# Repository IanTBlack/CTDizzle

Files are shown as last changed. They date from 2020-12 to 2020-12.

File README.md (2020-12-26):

# CTDizzle

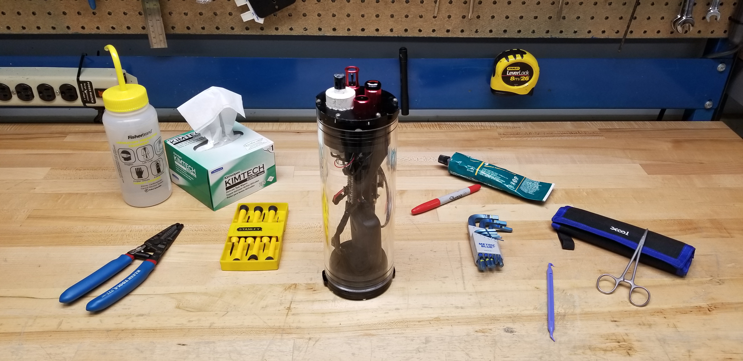
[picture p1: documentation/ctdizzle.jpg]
ctdizzle


Welcome! This is the repository for the CTDizzle, an open source CTD that is built on an Arduino platform. 
For those not familiar with the CTD instrument, it is a generic sensor type that measures water conductivity, temperature, and pressure. It is commonly used in the ocean.
By doing some math, these sensors can compute other data products like salinity, density, and depth. 
This information has a variety of applications in oceanography and fisheries research.

The CTDizzle framework is considered charityware. You can use and copy it as much as you like, but you are encouraged to make
a donation to the American Civil Liberties Union (www.aclu.org) or another charity of your choice if you find it useful.

For issues related to the CTDizzle, please use GitHub's issue tracker.

If you would like to contribute to this project, please submit a pull request or consider making your work public so that others may benefit.

For questions and more information, contact Ian Black (iantimothyblack@gmail.com). Please put "CTD" in the subject line so it doesn't go to spam.

Here are some other open source CTDs used under different applications:

Arduino-based Sonde: https://github.com/glockridge/DrifterApplication

OpenCTD: https://github.com/OceanographyforEveryone/OpenCTD

PiCTD: https://github.com/haanhouse/pictd

## CTDizzle Specifications
Maximum Sampling Rate: 1Hz

Tested Depth: 80m

Maximum Depth: 100m (Acrylic Tube), 200m (Aluminum Tube)

Conductivity Accuracy: +/- 2% (After Calibration)

Conductivity Response Time: 1s

Temperature Accuracy: +/- 0.1 degC

Temperature Response Time: 3s

Pressure Accuracy: +/- 100 mbar

Pressure Response Time: 20ms

Clock Accuracy: 29 PPM (+/- 3s per day)

Battery Life: Dependent (~60 hours @ 1Hz on a 3.7v 2200 mAh)

## How do I navigate this repository?

### ctdizzle
This folder contains the Arduino code for driving the instrument. The main sketch is the sketch titled "ctdizzle.ino". 
You may notice that there are other sketches called "temperature.ino" or "conductivity.ino". These are split files that are still part of the main sketch, but 
contain functions specific to a sensor or task. For example, "clock.ino" contains functions that will initialize the real-time clock and allow 
you to ask it for the date and time. These functions are then implemented in the setup() and loop() functions in the main sketch.

### documentation
This folder contains vendor datasheets, a spreadsheet containing a list of build materials, and a build guide.
There is also an example of a "config.txt" file, which allows you to adjust the sensor sampling rate when it is placed in the root direction of the data SD card.
Please note that many of the build materials such as solder, PLA filament, tools, and epoxy can be substituted for versions that you prefer. 
Remember that this is a guide and you can change things however you want. 
If you come up with a better solution or method, please consider contributing to the open source CTD concept by creating your own repository and instructions so that others may benefit.

### prints
This folder contains the 3D prints used in the CTDizzle. If you want to modify these parts, they are provided as .ipt files which can be used with Autodesk Inventor.
If you just want to print these parts yourself or through a vendor, you can use the .stl files and a slicer to create the necessary gcode.

Parts with the word "dremel" in the filename are intended to act as a guide when using a rotary tool to remove anodized finish on the end caps. 
These parts should be made of PLA.

Parts with the word "potting" in the filename are intended to act as a jig when using potting compound to permanently connect the conductivity probe to the endcap. 
These parts should be made out of water-soluble PVA.

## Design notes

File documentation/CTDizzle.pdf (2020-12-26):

# CTDizzle

## An Open Source CTD

### Version: 6.0.0

2020-12-26

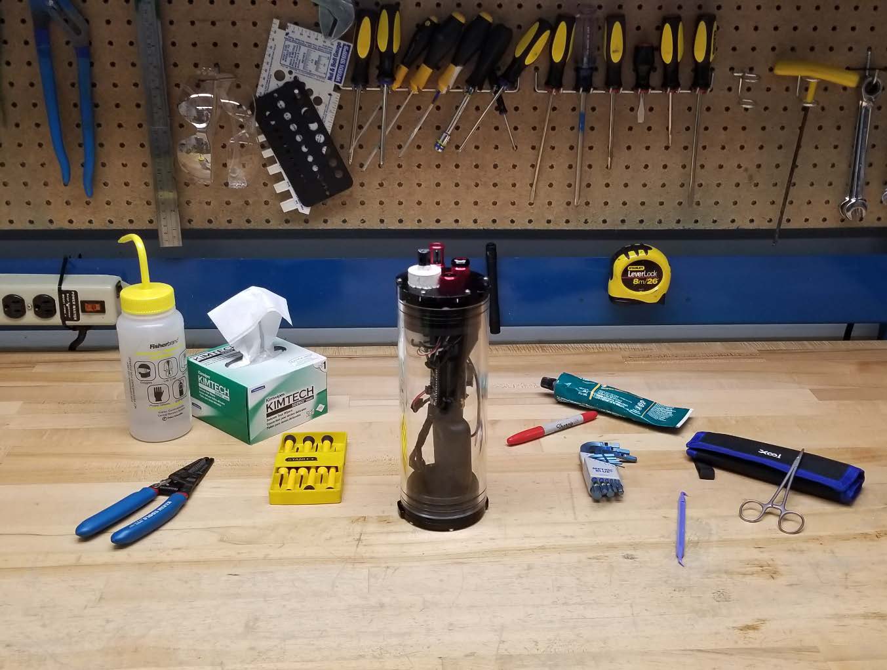
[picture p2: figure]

## Table of Contents

License | 1
Author’s Note | 1
CTDizzle Specifications | 2
Bill of Materials | 2
Other Open Source CTDs | 2
Required Skills and Experience | 2
O-rings | 2
Software Setup | 3
Arduino IDE | 3
Arduino Board | 3
Arduino Libraries | 3
Formatting the SD Card | 4
Uploading a Sketch | 4
Communication Protocols | 4
Pinouts | 5
Component Testing | 5
Building the CTDizzle | 6
Preparing the End Cap | 6
Potting the Probe | 9
Installing the Temperature, Pressure, and Switch | 12
Board Soldering | 13
3D Printed Board Mount | 14
Making the Switch Cable | 14
config.txt | 15
Bench Testing | 15
Code | 17
board.ino | 17
error_cycle_led() | 17
get_voltage() | 17
initialize_comms(bps,i2c_clock) | 17
power_board_led(state) | 17
power_leds(state) | 17

wait_for_serial(seconds) | 17
clock.ino | 17
get_datetime() | 17
get_unixtime() | 18
initialize_rtc() | 18
conductivity.ino | 18
get_conductivity() | 18
power_ec_led(state) | 18
ctdizzle.ino | 18
setup() | 18
loop() | 18
eos80.ino | 18
compute_depth(relative_pressure,latitude) | 18
compute_salinity(conductivity,temperature,relative_pressure) | 19
compute_density_anomaly(salinity, temperature, relative_pressure) | 19
pressure.ino | 19
get_absolute_pressure() | 19
get_relative_pressure(atmospheric) | 19
initialize_pressure() | 19
sd.ino | 19
initialize_logger() | 19
log_data(dt,ec,t,p,v) | 19
make_directory() | 19
make_file() | 20
read_config() | 20
set_file_creation_datetime() | 20
temperature.ino | 20
get_temperature() | 20
initialize_temperature() | 20
Conductivity Calibration | 20
Temperature Compensation | 20
Things to Think About | 21
Corrosion | 21

Batteries and Charging | 21
Data Quality | 21

1

## License

MIT License

Copyright (c) 2017 Ian Black

Permission is hereby granted, free of charge, to any person obtaining a copy of this software and associated documentation files (the "Software"), to deal in the Software without restriction, including without limitation the rights to use, copy, modify, merge, publish, distribute, sublicense, and/or sell copies of the Software, and to permit persons to whom the Software is furnished to do so, subject to the following conditions:

The above copyright notice and this permission notice shall be included in all
copies or substantial portions of the Software.

THE SOFTWARE IS PROVIDED "AS IS", WITHOUT WARRANTY OF ANY KIND, EXPRESS OR IMPLIED, INCLUDING BUT NOT LIMITED TO THE WARRANTIES OF MERCHANTABILITY, FITNESS FOR A PARTICULAR PURPOSE AND NONINFRINGEMENT. IN NO EVENT SHALL THE AUTHORS OR COPYRIGHT HOLDERS BE LIABLE FOR ANY CLAIM, DAMAGES OR OTHER LIABILITY, WHETHER IN AN ACTION OF CONTRACT, TORT OR OTHERWISE, ARISING FROM, OUT OF OR IN CONNECTION WITH THE SOFTWARE OR THE USE OR OTHER DEALINGS IN THE SOFTWARE.

## Author’s Note

You can use and copy any part of the CTDizzle as much as you like, but you are encouraged to make a donation to the American Civil Liberties Union (www.aclu.org) or any charity of your choice if you find it useful.
This guide operates under the assumption that you are using parts found within the Bill of Materials. This guide is not foolproof and the author acknowledges that there are likely better ways to build an open source CTD. The author has also made many expensive mistakes while iterating each build and recognizes that builders may make similar mistakes if not treading lightly. If you are unsure of how to perform a task, please take the time to research methods and practice skills. If you come up with a simpler or better way to complete a task, please share that knowledge!
If at any time you have questions, concerns, or need guidance, please to do not hesitate to contact: Ian Black
iantimothyblack@gmail.com

## CTDizzle Specifications

Maximum Sampling Rate: 1Hz
Tested Depth: 80m
Maximum Depth: 100m (Acrylic Tube), 200m (Aluminum Tube) Conductivity Accuracy: +/- 2% (After Calibration)
Conductivity Response Time: 1s
Temperature Accuracy: +/- 0.1 degC
Temperature Response Time: 3s
Pressure Accuracy: +/- 100 mbar
Pressure Response Time: 20ms
Clock Accuracy: 29 PPM (+/- 3s per day)
Battery Life: Dependent (~60 hours @ 1Hz on a 3.7v 2200 mAh)

## Bill of Materials

A complete list of parts used, cost, and quantities can be found in the CTDizzle GitHub repository under the documentation folder in a file called BoM.ods.

## Other Open Source CTDs

Arduino-based Sonde: https://github.com/glockridge/MooredApplication
Oceanography For Everyone OpenCTD: https://github.com/OceanographyforEveryone/OpenCTD PiCTD: https://github.com/HaanHouse/PiCTD

## Required Skills and Experience

The construction of any open source CTD requires some experience using tools such as a soldering iron, wire strippers, drill, screwdriver, and wrench. If you are unfamiliar with soldering, it is highly
recommended that you practice the lineman’s splice on a piece of scrap wire and through-hole soldering on a piece of protoboard.
The CTDizzle in particular requires some experience 3D printing with Polylactic Acid (PLA) and Polyvinyl Alcohol (PVA) filaments. If you are following along with this guide, you will also be required to mix and place epoxies.
O-rings
The Blue Robotics components of this CTD build require you to be familiar with O-ring inspection and installation. Clean and greased O-rings are paramount to the success of a CTD deployment in the ocean. To inspect and install an O-ring…
1. Wash and dry your hands.
2. Use isopropyl alcohol and lint-free wipes to clean the O-ring.
3. Under a light source, lightly stretch the O-ring and use your fingers to feel and observe for any damage.
4. Apply a light amount of silicone grease to the O-ring before installation.
5. Use an O-ring pick to install the O-ring.

## Software Setup

Arduino IDE
The Arduino Integrated Development Environment (IDE) is simple to use and allows you to quickly upload code to a board that understands Arduino. If you are new to Arduino, it is recommended that you set up the Arduino IDE using the default directories that the download wizard creates.
To install the IDE…
1. Go to https://www.arduino.cc/en/software to download the Arduino IDE installer that works best with your operating system.
2. Follow the installation wizard.
3. Hooray! You can now use the IDE.

Arduino Board
There are many different types of Arduino boards out there and not all are supported by default within the Arduino IDE. In order to get the Adafruit Feather M0 Basic Proto to work, we need to make sure the IDE knows what to look for by installing the right package.
To set up the M0…
1. Open the Arduino IDE.
2. Navigate to Tools > Board > Boards Manager.
3. In the search bar, type in Adafruit SAMD Boards
4. In the window, select Adafruit SAMD Boards. Confirm the Adafruit Feather M0 is in the list of boards included in the package.
5. Ensure the version is the most recent version.
6. Select Install.

Arduino Libraries
The CTDizzle requires the installation of Arduino libraries that help you communicate with each sensor. Libraries contain sets of functions that simplify the development process and allow you to focus more on higher level coding. In order to operate the CTDizzle, you will need to install several third-party libraries. Conveniently, they can be installed via the Arduino IDE.
Table 1: Third-party Arduino Libraries
Library Name | Developer | GitHub Repo
RTClib | Adafruit | https://github.com/adafruit/RTClib
BlueRobotics MS5837 Library | Blue Robotics | https://github.com/bluerobotics/BlueRobotics_MS5837_Library
BlueRobotics TSYS01 Library | Blue Robotics | https://github.com/bluerobotics/BlueRobotics_TSYS01_Library
To install these libraries…
1. Open the Arduino IDE.
2. Navigate to Tools > Manage Libraries.
3. Search for each library by name.
4. Install the most recent version.

Formatting the SD Card
It is also necessary to format the microSD card so that it can be used to store data. You can do this using the native formatter utility for your operating system, but it is recommended that you utilize the SD Memory Card Formatter tool developed by the SD Association.
To download the SD Memory Card Formatter…
1. Go to https://www.sdcard.org/downloads/formatter/
2. Download the correct tool for your operating system.
3. Follow installation instructions.
To format your card…
1. Insert your card into your computer. Make sure it appears in your file explorer.
2. Open the SD Card Formatter tool.
3. Select your card.
4. Select Quick Format.
5. Name your card if you want.
6. Select Format.

Uploading a Sketch
Uploading a code (aka sketch) is simple to do with the Arduino IDE. To upload a sketch…
1. Open the Arduino IDE.
2. Make sure the sketch you want to upload is in the window.
3. Navigate to Tools > Board and select Adafruit Feather M0.
4. Navigate to Tools > Port and select the port that has the Adafruit Feather M0.
5. Navigate to Sketch > Upload. (or hit CTRL + U, or select the right-pointing arrow)
6. Wait for the sketch to compile and upload!

## Communication Protocols

All the sensors in this CTD build use the inter-integrated circuit (I2C) serial communication protocol. This means that each sensor can be on the same send and receive data lines. Each sensor has its own address, which prevents confusion when talking to multiple sensors. For the sake of simplicity, the operating code for this CTD waits for one sensor to respond and send data before talking to the next sensor.
The SD card module of the Adalogger Featherwing operates under the Serial Peripheral Interface (SPI) protocol. Like I2C, multiple sensors can be connected on the same lines send and receive lines. However, SPI requires that each sensor be connected to its own chip select, thus taking up more pins compared to I2C. Conveniently, the SD card module in this build is the only component that operates under SPI.
The Atlas Scientific EC EZO can operate under I2C or Universal Asynchronous Receive Transmit (UART). By default, the EC EZO is shipped in UART mode. You can review the Atlas Scientific manual to change it to I2C mode either via software or manually. Each protocol has its advantages and disadvantages, but the CTD operating code assumes that the EC EZO is in I2C mode.

## Pinouts

Each sensor wire/pin should be connected to the controller board pin as described by the table below. Note that each Blue Robotics sensor is 3.3V tolerant. If you connect one of those sensors to a 5V pin, you risk damaging it. The Atlas Scientific EC EZO can be connected to 3.3V or 5V. The Adalogger Featherwing SD module is automatically connected when you stack it on top of the Feather M0. The chip select just needs to be specified in the operating code.
Table 2: Sensor Pinouts
Blue Robotics TSYS01 Temperature Sensor | Adafruit Feather M0
Black Wire | GND
Red Wire | 3V
Yellow Wire | SDA
Green Wire | SCL
Blue Robotics MS5837 Pressure Sensor | Adafruit Feather M0
Black Wire | GND
Red Wire | 3V
Yellow Wire | SDA
Green Wire | SCL
Atlas Scientific EC EZO or Carrier Board | Adafruit Feather M0
GND | GND
VCC | 3V
SDA/TX | SDA
SCL/RX | SCL
Adalogger Featherwing SD Module | Adafruit Feather M0
CS | 10

## Component Testing

# Please inspect and test each component

before soldering and install.

# Vendor guides can be found in the documentation folder of the GitHub

repository.

## Building the CTDizzle

Preparing the End Cap
In order to pot the Atlas Scientific Conductivity probe to the end cap, you must drill out one of the holes to 12mm. In the following pictures, the side facing up is the “external” side and the side facing down is the “internal” side. “External” implies that it is going to be exposed to seawater.
In the left image orientation, the 12mm hole was drilled into the upper right hole using a 12mm drill bit. The hole was then deburred. You will want to test fit the conductivity probe in the newly drilled hole. If you are unable to insert it, use a round file to increase the diameter of the hole slightly. The conductivity probe should fit snugly and require some force to insert and remove.

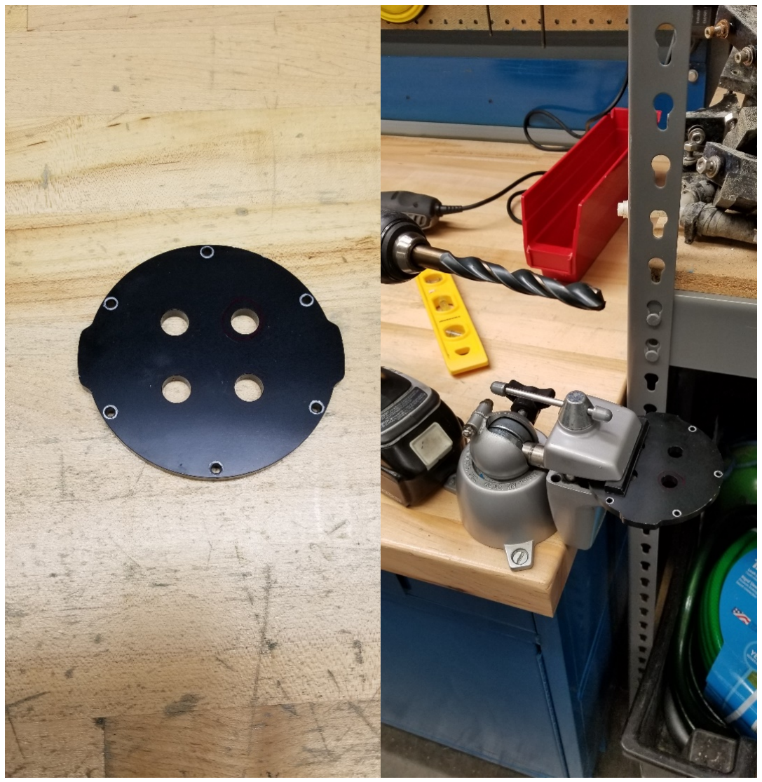
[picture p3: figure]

Figure 1: End cap 12mm hole placement.

Next attach the dremel_internal and dremel_external 3D prints to the endcap using some M3 screws and nuts. Notice that the internal and external 3d prints result in holes that are different shapes. The internal print will produce an irregularly shaped outline to accommodate the internal diameter of the end cap flange.

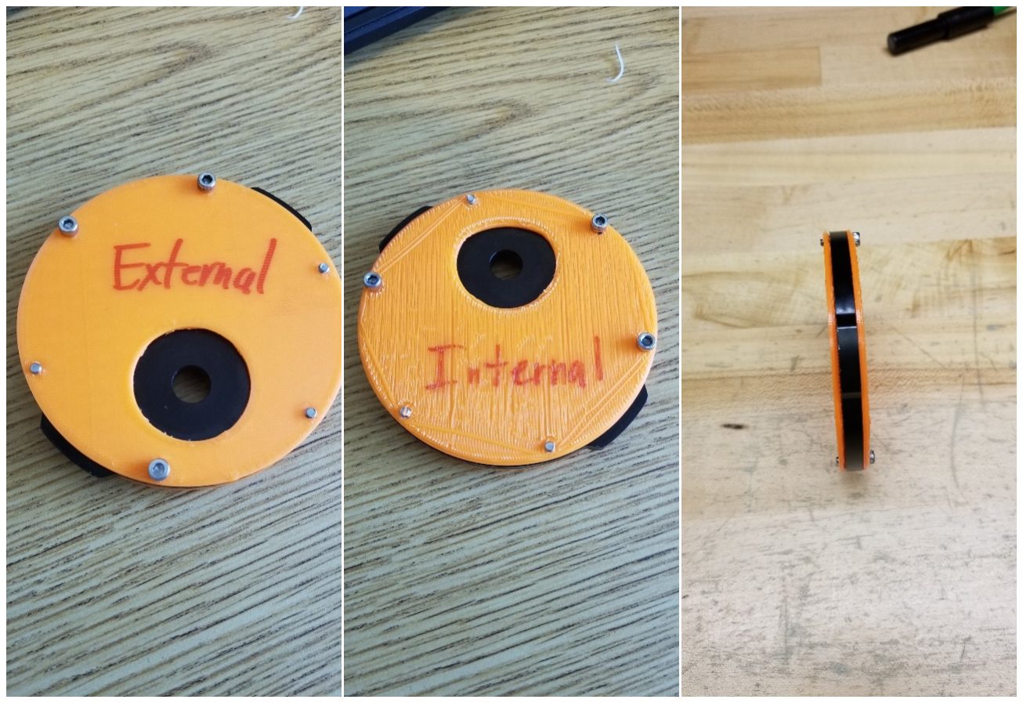
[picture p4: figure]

Figure 2: Rotary tool jig placement.

Using a Dremel or similar rotary tool, remove the exposed anodization. This can be done using a grindstone bit or sandpaper attachment. You should remove the anodization to the point where you see exposed aluminum and the surface finish is rough. This will facilitate better adhesion of the epoxy used to hold the conductivity probe in place.

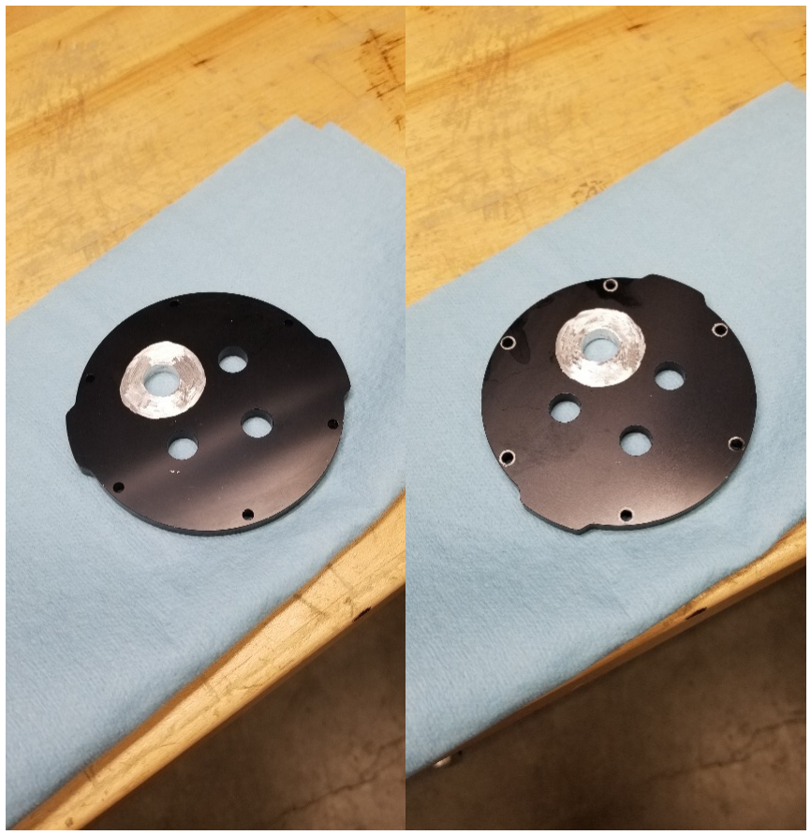
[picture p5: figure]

Figure 3: End cap after removal of anodization.

Potting the Probe
Test fit the probe in the 12mm hole. Using the PVA (potting_*) prints as guides, mark on the probe the height of the prints. Remove the probe from the end cap.
Using sandpaper, rough up the portions of the probe that will be in contact with epoxy. This will ensure better adhesion.
Clean the end cap and probe with isopropyl alcohol. Apply masking or electrical tape around the edge of the raw aluminum on both sides. This will help keep the potting compound in the appropriate area in case the PVA potting jig warps during use. Install the probe and wrap the sensor area in electrical tape to prevent epoxy leakage.

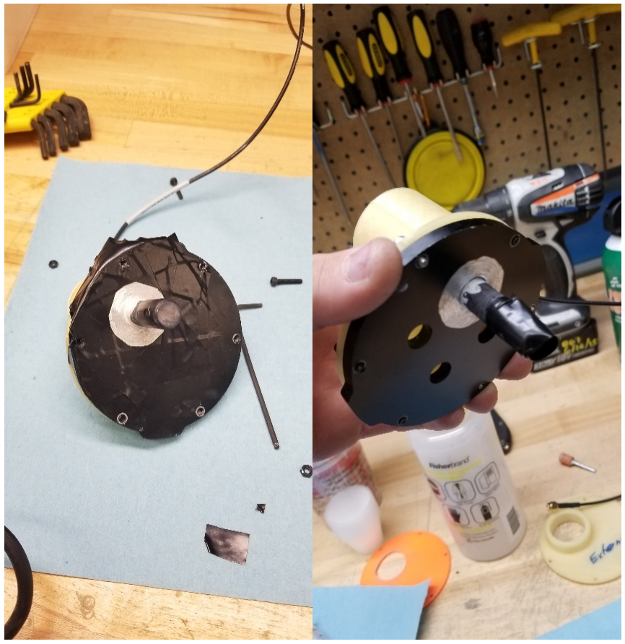
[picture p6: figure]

Figure 4: Taping of area around bare aluminum and probe end.

After installing the probe, install the potting_internal 3D print using some M3 screws to secure it to the end cap. Make sure it lines up with the correct side. You can support the end cap using a cup or mug. Once it is installed, mix and apply enough epoxy to fill the void to the rim. If bubbles appear, use a toothpick to remove them. Allow the epoxy to cure for 24-48 hours. Check the epoxy after a couple of hours to make sure that it has not leaked below the PVA jig. If it has, remove the jig and use isopropyl alcohol to clean up the epoxy.
After the internal side has cured, repeat the process with the external side.

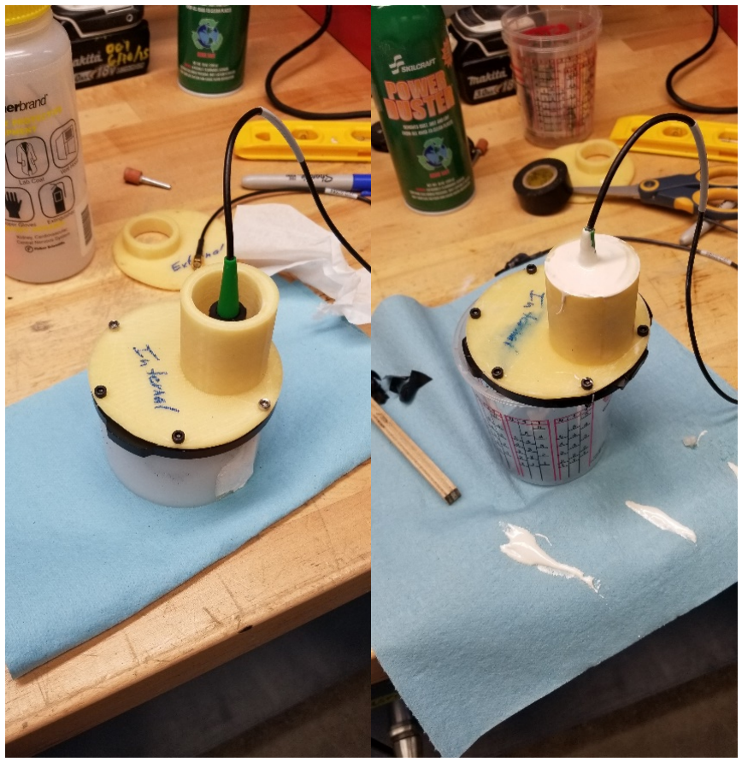
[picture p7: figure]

Figure 5: Installation of PVA jigs for epoxy application.

Once both sides have cured, place the setup up in a container of water. You may have to replace the water every few hours or so. Once the PVA 3D prints have dissolved way, clean up the epoxy with a scotch brite pad and a file to remove any burrs. Test fit the end cap flange to ensure they fit well together. If the epoxy make its way underneath the jig while curing, you can use a pair of hemostats or metal pick to remove the excess. Take care to not scratch the surface the end cap O-ring will seal to.

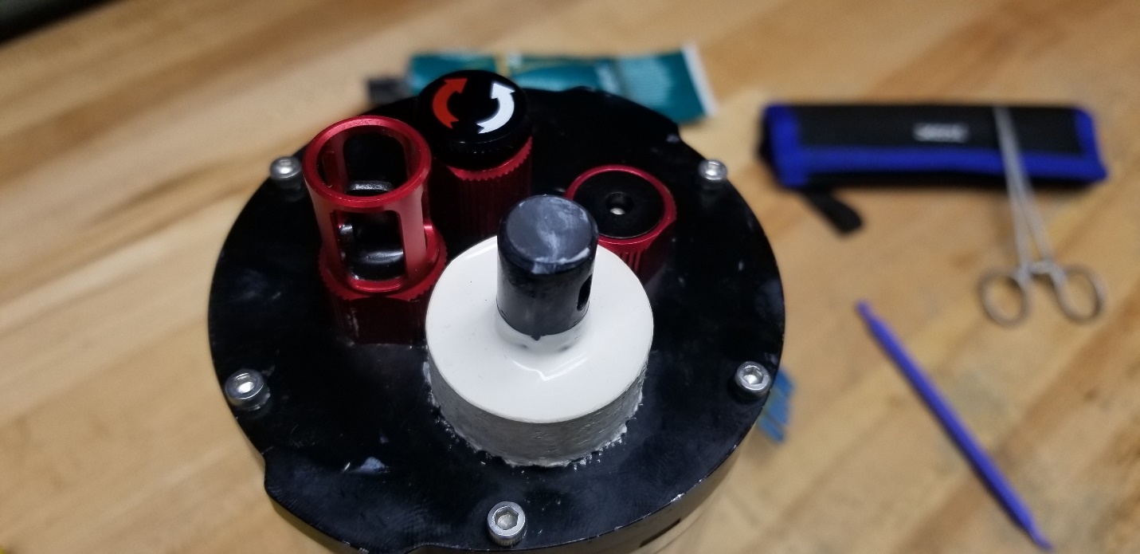
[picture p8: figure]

Figure 6: View of the external epoxy.

Installing the Temperature, Pressure, and Switch
Clean the end cap using isopropyl alcohol. Ensure the O-rings are clean and greased. The O-rings should be within the groove of each bulkhead and on the side of the end cap that is exposed to seawater. Insert each component into the end cap and add the nut. Tighten using a Blue Robotics tool or a crescent wrench. They should be tightened enough that you observe no gap between the bulkhead and end cap. In these pictures, the DF13 connectors are removed from the sensors. If you do not want to remove them, Blue Robotics offers a DF13->pinout board. If you opt to remove the connectors, cut them off as close to the connector as possible.

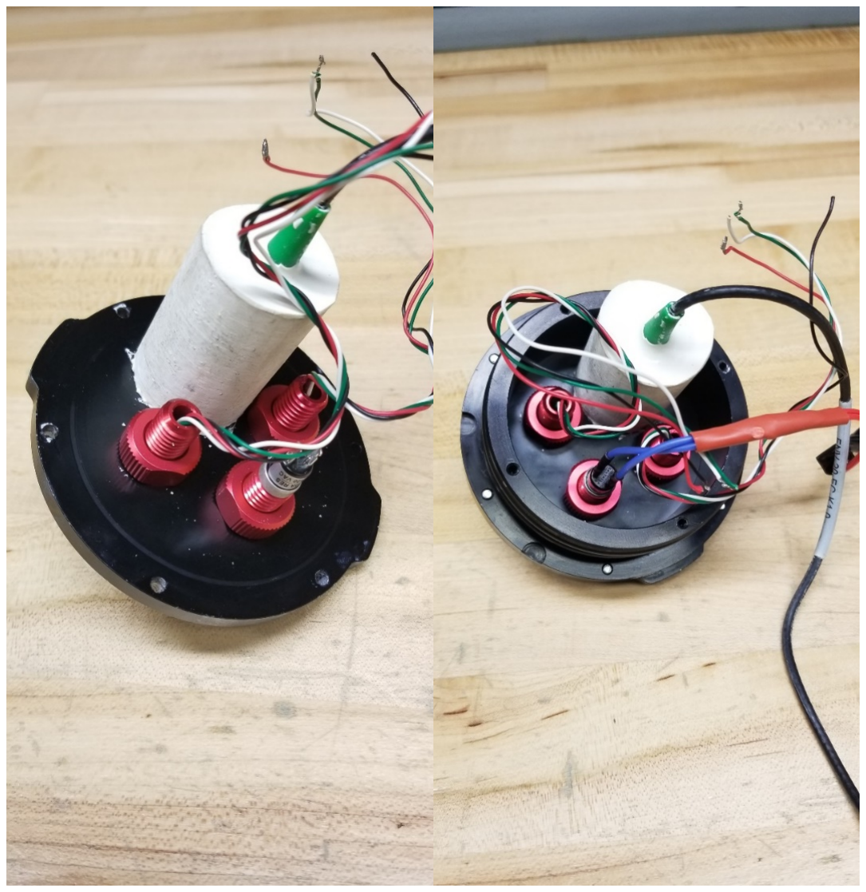
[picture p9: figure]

Figure 7: Installation of Blue Robotics sensors and switch.

Board Soldering
For access to the prototyping area, the M0 can be stacked on top of the Adalogger using stacking headers. The use of short feather headers allows for a more compact footprint. The first step is to solder a set of short male feather headers to the M0. A terminal block set can be installed in the prototyping area to make it easier to connect sensor wires to the board. You will need to solder wires from the GND, 3V, SCL, and SDA pins to the terminal block so that the conductivity, temperature, and pressure sensors can be connected to the board. The following pictures show one way to do that.

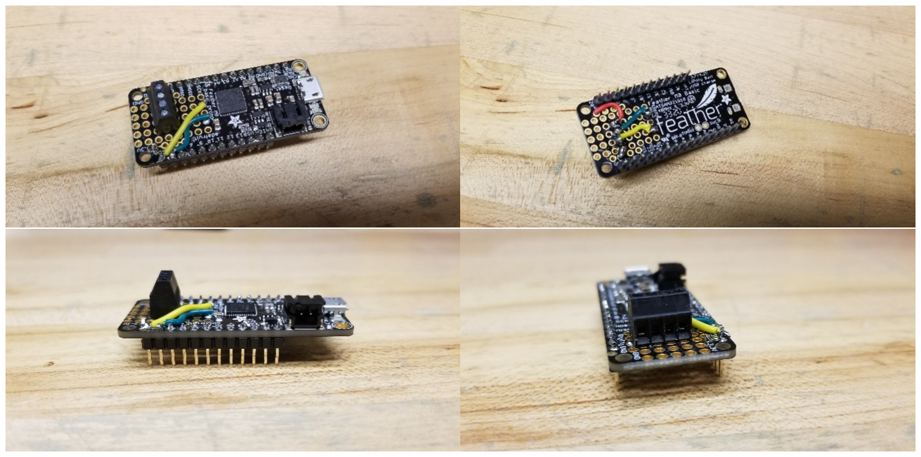
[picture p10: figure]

Figure 8: Soldering of male headers, wires, and terminal block to the Adafruit Feather M0 Proto

The Adalogger will stack below the M0. Next, solder a set of short female feather headers to the Adalogger. The following pictures show what the orientation should look like.

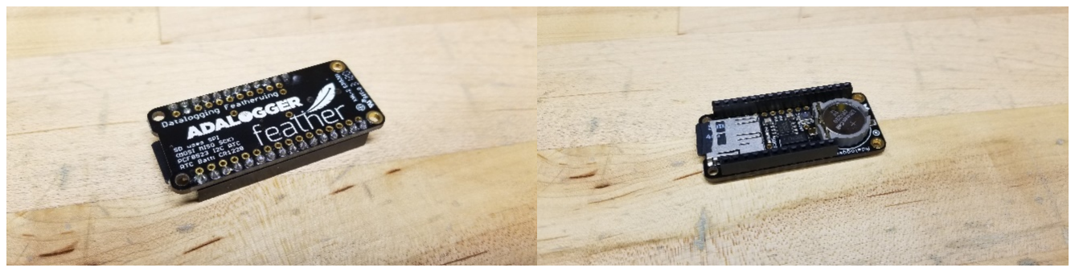
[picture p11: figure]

Figure 9: Soldering of female headers to the Adalogger Featherwing.

3D Printed Board Mount
The 3D printable mount allows you to mount the controller board stack and the Atlas Scientific EZO Isolation Board to the sensor flange. The mount is attached to the flange using 11mm M3 screws. The boards are attached to the mount using M2.5 thread nylon standoffs. This is one method of many to mount the electronics inside of the pressure case. Feel free to modify the drawings to suit your needs.

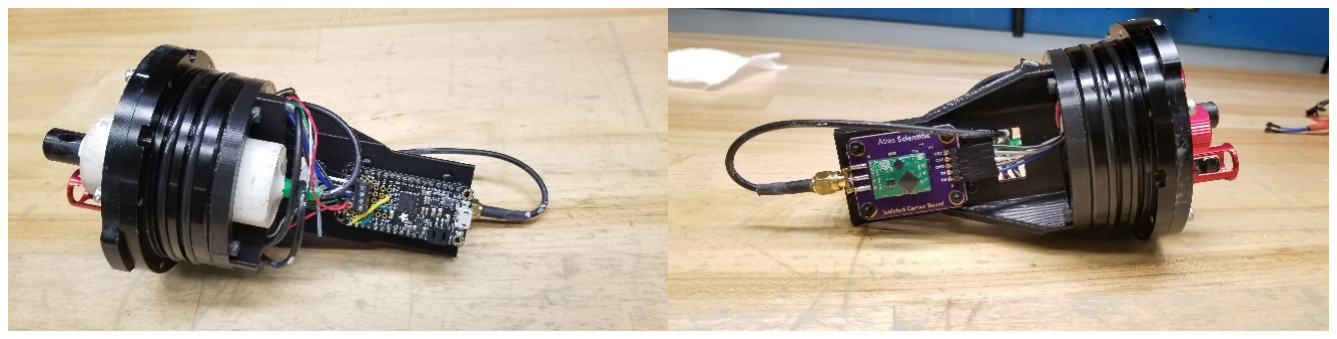
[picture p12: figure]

Figure 10: Attachment of the 3D printed mount. Making the Switch Cable
The addition of the Blue Robotics switch allows you to power cycle the sensor. This can help with conserving battery life and provides the ability to differentiate between profiles if using the CTD in a profiling fashion. If you are using a 5V rechargeable battery pack, you will need to splice the Blue Robotics switch wires into the V+ line on the USB cable.

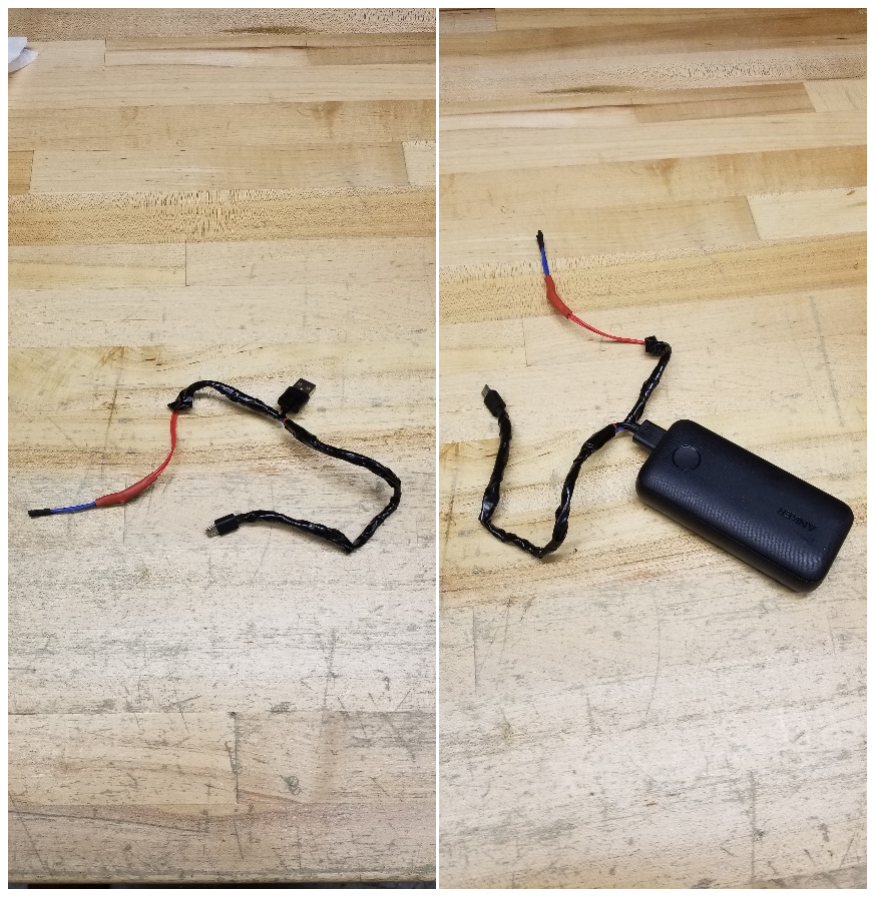
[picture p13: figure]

Figure 11: Example of a 5V USB cable splice to the switch

## config.txt

You have the option of placing a config.txt file on your microSD card. This file should contain only an integer on the first line that represents the number of seconds to wait in between samples. If unable to interpret the file, or if it doesn’t exist, the CTD will default to one sample per second.
If you want to adjust the sampling rate to one sample every 3 hours, you will need to create a config.txt file like the screenshot below and then place it in the root directory of your SD card.

## Bench Testing

Once all the wiring is complete. Upload the ctdizzle sketch to your board.
Navigate to Tools > Serial Monitor. The setup sequence will begin once serial communication is established or after 30 seconds (whichever comes first). You will see something like the screenshot below. Confirm that the clock time and sensor values are appropriate.

The first column is the datetime.
The second column is the conductivity, which should be zero if the sensor is in air.
The third column is the temperature. If this value is negative, check your SCL/SDA orientation.
The fourth column is the pressure, which should be zero or near zero in air.
The fifth column is the battery voltage. Since we are connected to the USB, this value is the voltage on the vbatt pin.

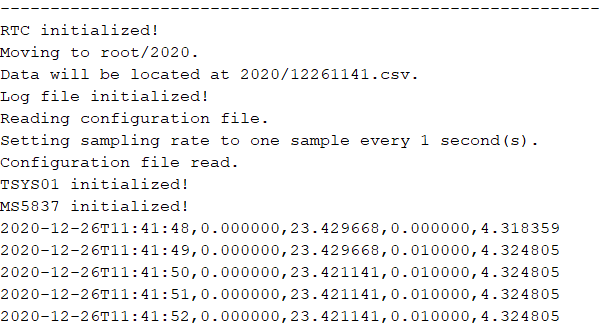
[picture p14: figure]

After you have let the unit run for a minute or so, disconnect the power and then insert the SD card into a reader device attached to a computer. Once you open the drive folder, the contents should look similar to the screenshot below. If you didn’t create a config.txt file previously, it won’t exist. If the year isn’t 2020, then the folder name will also be different.

Opening the folder titled by year will show files for each time you turned the unit on.

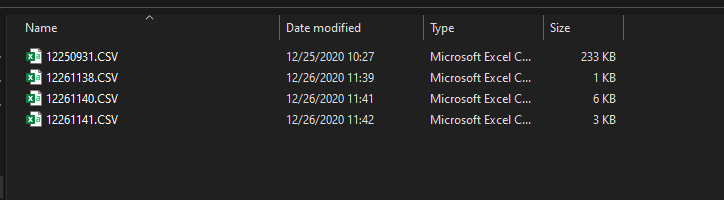
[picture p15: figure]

If we open the 12261141.CSV file, we see data that matches the output from the serial monitor.

## Code

The main sketch for operation is the ctdizzle.ino file found in the ctdizzle folder. You’ll notice that there are several .ino files in this folder, but they are all actually part of the same sketch! For more details on each function, please read the comments in the code.

board.ino
Upon upload, this sketch brings in the Wire and SPI libraries that allow the M0 to communicate to the sensors and clock.
error_cycle_led()
This function will turn the board LED on pin 13 on for 1 second and then off for 1 second.
It is usually put inside of a never-ending while loop and used as a visual indicator for an error. get_voltage()
This function will calculate the battery voltage on the vbatt_pin. For the Feather M0, this is pin A7. The voltage is returned as a float.
initialize_comms(bps,i2c_clock)
This function initialize serial communications so that the board can talk to sensors.
bps refers to bits per second, or the baud rate for serial communication between the board and the host computer. i2c_clock refers to the clock frequency for I2C communication. power_board_led(state)
This function will turn the board LED on pin 13 on or off, given a state. The state is either “ON” or “OFF”.
power_leds(state)
This function will turn the board and EC EZO LEDs on or off, given a state. The state is either “ON” or “OFF”.
wait_for_serial(seconds)
This function will wait for a serial connection to a terminal program on the host computer for X number of seconds before proceeding. While it is waiting, the board LED will cycle.

clock.ino
Upon upload, this sketch brings in the RTClib library that allows for communication with the clock on the Adalogger.
get_datetime()
This function returns the current date and time as a string in ISO-8601 format (YYYY-mm-ddTHH:MM:SS).

get_unixtime()
This function returns the current date and time as an integer in the number of seconds since 1970-01-01 00:00:00
initialize_rtc()
This function initializes the real time clock on the Adalogger. If the RTC has lost power and the board detects a serial connection to the computer, time is automatically updated. If no communication occurs with the clock, then the board error cycles the LED.

conductivity.ino
get_conductivity()
This function requests conductivity from the EC EZO and returns it as a float. There is a built-in wait time of 600ms to allow the EC EZO to perform its conversion.
power_ec_led(state)
This function will turn the EC EZO LED on or off, given a state. The state is either “ON” or “OFF”.

ctdizzle.ino
This is the main sketch for CTD operation. It contains the setup and loop functions. atmospheric_pressure is globally declared because it is used to “zero” the pressure sensor. This is of course operating under the assumption that you turned the sensor on above water and near sea level. interval is also globally declared. This value is pulled from a config.txt file located on the SD card. If no config file is found, then the interval defaults to 1. The CTD will then sample once per second.
setup()
This function initializes all sensors and sets up logging files.
loop()
This function will request data from each sensor and then save it to a log.
At the beginning of the loop, the number of milliseconds since the microcontroller started is recorded, then operations are performed, and the number of milliseconds since the microcontroller started is sampled again. The difference between these values is then subtracted from the interval value. This provides more accurate timing between samples.

eos80.ino
This sketch provides functions for computing depth, salinity, and density anomaly. compute_depth(relative_pressure,latitude)
Computing depth requires that relative pressure be in decibars and that the latitude be defined. The return for this function is depth in meters.

compute_salinity(conductivity,temperature,relative_pressure)
Computing salinity requires conductivity in uS/cm, temperature in degC, and relative pressure in decibars. The return for this function is salinity in PSU.
compute_density_anomaly(salinity, temperature, relative_pressure)
Computing density requires salinity, temperature, and relative pressure. The return for this function is the density anomaly relative to 1000 kg/m3.

pressure.ino
This sketch provides functions for controlling the MS5837 pressure sensor.
get_absolute_pressure()
This function will return the total pressure reading (including the pressure exerted by the atmosphere). The return is in milibars. There is a built in delay of 50ms to allow for the pressure sensor to perform conversions.
get_relative_pressure(atmospheric)
This function removes consideration of atmospheric pressure and returns the water column pressure in decibars. You will need to supply the atmospheric pressure. This can be done by taking a pressure sample on start-up, assuming the unit is above water, or by using a standard atmospheric pressure of 1013.25 mbar.
initialize_pressure()
This function initializes the pressure sensor.

sd.ino
This sketch provides functions for setting up the SD card and creating log files. Upon upload, the necessary libraries and files are defined.
initialize_logger()
This function initializes the SD card module, reads the config file (if it exists), makes a new directory(if needed) and creates a new file to log to.
log_data(dt,ec,t,p,v)
This function logs data to a csv file. To alter the order of logging you will need to modify the function defined in loop(), the formatting in log_data() and the header string in make_file(). make_directory()
This function creates a new directory on the SD card that is titled by the current year. If the folder already exists, then nothing exciting happens.

make_file()
This function creates a new log file on power cycle. Data is saved to this file in a format defined by the header string in this function and the log_data() function. The file is named by the date and time that it was created. It is in the format of mmddHHMM.csv
read_config()
This function reads from a simple configuration file (config.txt) located in the root directory of the SD card. Currently, this config.txt file can only consist of a single integer, which then determines the number of seconds in between samples. If no config.txt file is found, the number of seconds in between samples defaults to 1s.
set_file_creation_datetime()
This is a function that assigns a date and time attribute to the created log file so that it is easier to identify datafiles when using a file explorer. This function is called within the initialize_logger() function.

temperature.ino
This sketch contains functions for driving the TSYS01 temperature sensor.
get_temperature()
This function requests temperature from the TSYS01. There is a built-in 50ms delay to allow the sensor to perform its conversion.
initialize_temperature()
This function initializes the TSYS01.

## Conductivity Calibration

You can calibrate the conductivity sensor using methods as outlined by the Atlas Scientific User Manual. Atlas Scientific provides code examples on GitHub. https://github.com/Atlas-Scientific/Ezo_I2c_lib

Temperature Compensation
It should be noted that temperature plays a significant role in calibrating a conductivity probe. The CTDizzle code does not implement temperature compensation for conductivity, so that functionality must be added. The Atlas Scientific EC EZO offers temperature compensation of conductivity, but anecdotally this has been problematic. Atlas Scientific has not provided information on how this compensation is performed.

## Things to Think About

Corrosion
The Blue Robotics end caps are made of anodized aluminum and the provided screws are made of 316 stainless steel. Two contacting dissimilar metals in seawater effectively form a battery. The metal lower on the galvanic series scale (the anode) will corrode before the metal higher in the series (the cathode). Stainless steel is higher on the scale than aluminum so the aluminum end cap will corrode first. Anodization of the aluminum helps prevent this a little, but over time repeated removal and installation of the stainless screws can damage the anodization, exposing raw aluminum to seawater. It is recommended that you inspect the end cap before each deployment for signs of corrosion. You can also prevent corrosion by adding an anode that is lower on the galvanic series than aluminum. A chunk of zinc is a common anode used on oceanographic equipment.
Anoxic corrosion of the 316 stainless screws is also possible. Anoxic refers to a lack of oxygen in the seawater. Stainless will severely corrode in anoxic environments if left for a significant amount of time. If the CTD has been deployed for a long amount of time, it is recommended that you inspect the screws for corrosion. A corroded screw can lead to loosening of the end cap and reduction in the effectiveness of the O-ring, leading to flooding of the sensor.

Batteries and Charging
The Adafruit Feather M0 has a built-in 3.7V Lithium Polymer battery charger. In order to charge a battery, the board must be connected to a 5V source via the microUSB connector. The board can also be powered with an 5V source, such as a rechargeable battery pack intended for charging cell phones. These types of battery packs must be connected to the microUSB connector. These above directions describe how to create a switch cable for a 5V rechargeable battery pack, but you can do the same for a 3.7V LiPo. The JST Battery Extension Cable found in the Bill of Materials will allow you to do this without modifying the battery cable.
This iteration of the CTDizzle does not consider power savings. You can likely improve battery life by forcing the controller and peripherals to enter low power states when not in use.

Data Quality
If you are familiar with commercially available CTDs, you’ll notice that the CTDizzle does not compare in terms of accuracy, response times, and resolution. This problem does not necessarily preclude any open source CTD from being used in scientific study, but it does pose a challenge, particularly where high accuracy and resolution is needed. Currently there is a lack of robust calibration and quality
conformance procedures for the CTDizzle and other open source CTDs.

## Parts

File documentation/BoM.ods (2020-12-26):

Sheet: Parts
Prices as of 2020-12-26
Total | $797.60
Part/Consumable | Price Per Unit (USD) | Quantity | Subtotal (USD) | Note
Adafruit M0 Basic Proto | $19.95 | 1 | $19.95 | SAMD21
Adafruit Adalogger Featherwing | $13.95 | 1 | $13.95 | SD and RTC
Atlas Scientific Conductivity Kit K1.0 (https://atlas-scientific.com/kits/conductivity-k-1-0-kit/) | $214.99 | 1 | $214.99 | Includes mini probe, jumpers, driving circuit, isolation board, and calibration standards.
Blue Robotics Celsius Temperature Sensor (https://bluerobotics.com/store/sensors-sonars-cameras/sensors/celsius-sensor-r1/) | $60.00 | 1 | $60.00 | Includes O-ring.
Blue Robotics Bar30 Pressure Sensor (https://bluerobotics.com/store/sensors-sonars-cameras/sensors/bar30-sensor-r1/) | $72.00 | 1 | $72.00 | Includes O-ring.
Blue Robotics 3” Flange (https://bluerobotics.com/store/watertight-enclosures/3-series/o-ring-flange-3-series/) | $24.00 | 2 | $48.00 | Includes O-rings.
Blue Robotics 3” End Cap – No Holes (https://bluerobotics.com/store/watertight-enclosures/3-series/wte3-m-end-cap-r1/) | $10.00 | 1 | $10.00 | Includes O-rings.
Blue Robotics 3” End Cap – 4 Holes (https://bluerobotics.com/store/watertight-enclosures/3-series/wte3-m-end-cap-4-hole-r1/) | $12.00 | 1 | $12.00 | Includes O-rings.
Blue Robotics 3” Acrylic Tube – 11.75” (https://bluerobotics.com/store/watertight-enclosures/3-series/wte3-p-tube-12-r1/) | $86.00 | 1 | $86.00
Blue Robotics Switch (https://bluerobotics.com/store/comm-control-power/switch/switch-10-5a-r1/) | $15.00 | 1 | $15.00 | Includes O-rings and connector wires.
Loctite Marine Epoxy (https://www.amazon.com/gp/product/B00KH62K50/ref=ppx_yo_dt_b_asin_title_o07_s00?ie=UTF8&psc=1) | $5.50 | 6 | $33.00 | 0.85 Fl Oz Syringe
Hex M3 Nuts/Bolts Pack (https://www.amazon.com/gp/product/B078V3YCF6/ref=ppx_yo_dt_b_asin_title_o09_s00?ie=UTF8&psc=1) | $16.00 | 1 | $16.00 | Multiple uses. For securing 3D print to flange. Can ask Blue Robotics for extras if you don’t want to buy the whole pack.
SainSmart 1.75mm PVA – 0.5kg (https://www.amazon.com/gp/product/B00SSXAET8/ref=ppx_yo_dt_b_asin_title_o06_s00?ie=UTF8&psc=1) | $41.06 | 1 | $41.06 | Multiple prints. Water soluble.
Left-angle MicroUSB (https://www.amazon.com/gp/product/B003YKX6W2/ref=ppx_yo_dt_b_asin_title_o07_s00?ie=UTF8&psc=1) | $3.45 | 1 | $3.45 | Use this to hook up a 5v power pack if you go that route.
Hatchbox 1.75mm PLA – Any Color (https://www.amazon.com/HATCHBOX-3D-Filament-Dimensional-Accuracy/dp/B00J0EE1D4) | $20.00 | 1 | $20.00 | Multiple prints.
Kester 44 Rosin Core Solder (https://www.amazon.com/Kester-24-6337-0010-Rosin-Solder-SPOOL/dp/B00068IJWC) | $37.00 | 1 | $37.00 | Multiple uses. Any solder works.
4-Pin Terminal Block (https://www.adafruit.com/product/2137) | $1.55 | 1 | $1.55 | Use this to hook up to the EC EZO isolation board.
22AWG Solid Core Wire (https://www.adafruit.com/product/290) | $2.95 | 1 | $2.95 | Multiple uses. Any small wire works.
Short Feather Header – Female (https://www.adafruit.com/product/2940) | $1.50 | 1 | $1.50
Short Feather Header – Male (https://www.adafruit.com/product/290) | $0.50 | 1 | $0.50
JST Battery Extension Cable (https://www.adafruit.com/product/1131) | $1.95 | 1 | $1.95 | Use this to hook up a LiPo to the system if you go that route.
Li-Ion Battery Pack 3.7V 4400mAh (https://www.adafruit.com/product/354) | $19.95 | 1 | $19.95 | Use this or the 5V pack. Or you can do both.
Rechargeable Battery Pack 5V 10000mAh (https://www.adafruit.com/product/1566) | $39.95 | 1 | $39.95 | Use this or the 3.7V LiPo. Or you can do both.
Adafruit Black Nylon M2.5 Stand-off Set (https://www.adafruit.com/product/3299) | $16.95 | 1 | $16.95 | For securing boards to 3D prints.
CR1220 Coin Cell (https://www.adafruit.com/product/380) | $0.95 | 1 | $0.95 | For RTC.
4GB MicroSD Card (https://www.amazon.com/Sandisk-MicroSDHC-Memory-Card-Adapter/dp/B000SMVQK8) | $8.95 | 1 | $8.95

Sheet: Tools
Tool | What Ian Used | Notes
3D Printer | Creality Ender Pro 5 (https://creality3d.shop/collections/ender-series-3d-printer/products/creality3d-ender-5-pro-3d-printer) | Any printer will probably do.
Rotary Tool | Dremel (https://www.homedepot.com/p/Dremel-Lite-7760-4-Volt-Variable-Speed-Lithium-Ion-Cordless-Rotary-Tool-Kit-with-10-Accessories-7760-N-10/309740749) | Any rotary tool that has grinding or sanding attachments will do.
Flush Cutters | CHP170 (https://www.adafruit.com/product/152) | Wire strippers will likely perform the same functionality.
Soldering Iron | XYTronic-258 (https://www.adafruit.com/product/180) | Any soldering iron would do.
Drill | Milwaukee M18 Drill (https://www.homedepot.com/p/Milwaukee-M18-18-Volt-Lithium-Ion-Brushless-Cordless-1-2-in-Compact-Drill-Driver-with-1-2-0-Ah-Battery-Charger-and-Tool-Bag-2801-2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) | Any drill would do.
12mm Bit | uxcell 12mm (https://www.amazon.com/gp/product/B082D9FLX6/ref=ppx_yo_dt_b_asin_title_o09_s00?ie=UTF8&psc=1) | Needs to be 12mm for the conductivity probe.
Assorted Screwdrivers | 65 Piece Screwdriver Set (https://www.adafruit.com/product/829) | Any set of small screwdrivers will do.
Wire Strippers | Multi-use Wire Stripper (https://www.adafruit.com/product/147) | Make sure it works for 22 AWG wire.

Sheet: Software
Software
Arduino IDE (https://www.arduino.cc/en/software)
TeraTerm (https://ttssh2.osdn.jp/index.html.en)
Libre Office (https://www.libreoffice.org/)
SD Association Card Formatter (https://www.sdcard.org/downloads/formatter/)
Arduino Library | Installation Method
Wire | Native
SPI | Native
RTCLib | Available via Manage Libraries
MS5837 | Available via Manage Libraries
TSYS01 | Available via Manage Libraries
SD | Available via Manage Libraries

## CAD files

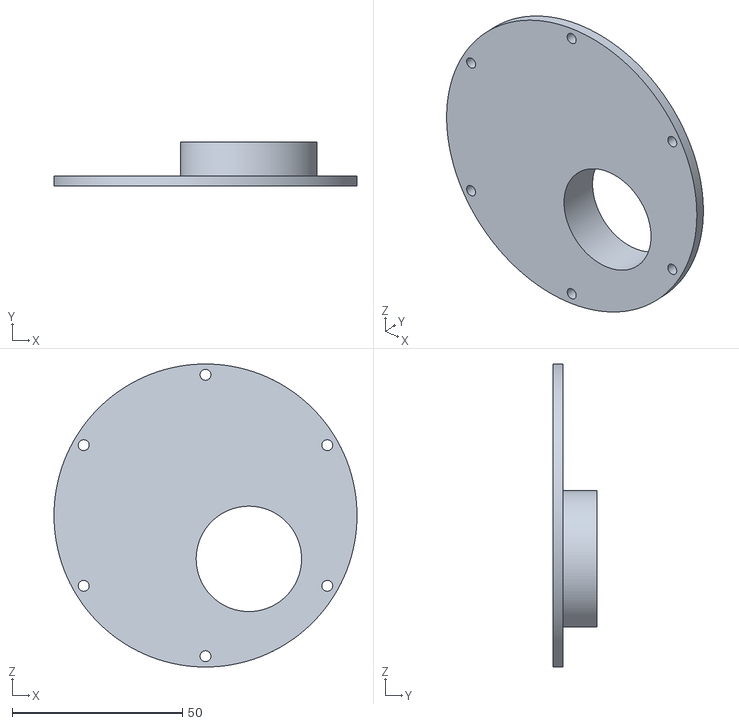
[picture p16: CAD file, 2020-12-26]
prints/stl/potting_external.stl
88.9 x 13.0 x 88.9

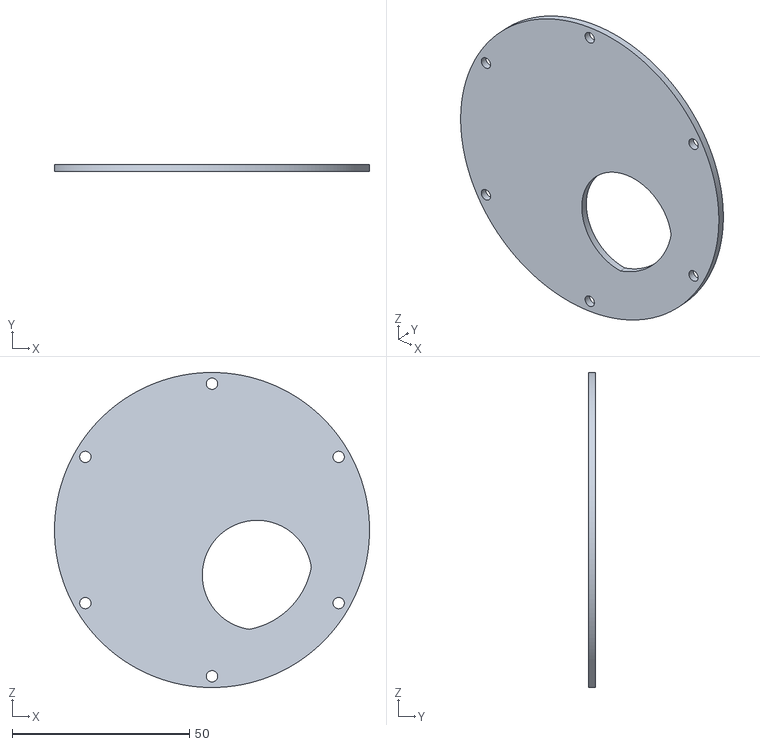
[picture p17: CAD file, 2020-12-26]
prints/stl/dremel_internal.stl
88.9 x 2.00 x 88.9

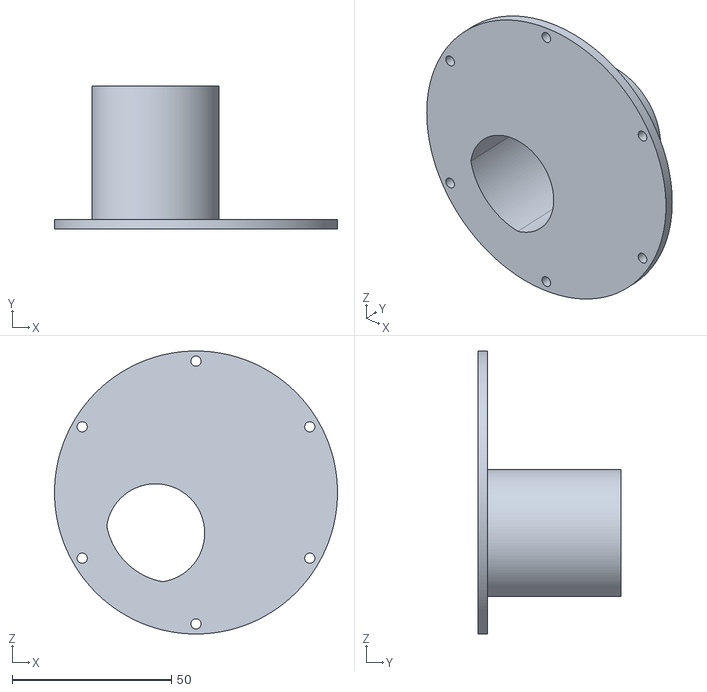
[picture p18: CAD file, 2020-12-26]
prints/stl/potting_internal.stl
88.9 x 45.0 x 88.9

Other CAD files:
prints/stl/dremel_external.stl
prints/ipt/dremel_external.ipt
prints/ipt/dremel_internal.ipt
prints/ipt/potting_external.ipt
prints/ipt/potting_internal.ipt

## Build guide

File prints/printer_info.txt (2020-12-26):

The prints in this folder were printed on a Creality Ender Pro 5 with Ultimaker 4.7 as the slicer.

PLA Settings
Extruder Temp: 205C
Bed Temp: 55C
Speed: 80mm/s
Z-Hop: Enabled
Supports: Enabled, 45deg
Bed Adhesion: Raft

PVA Settings 
---Applied masking tape to build plate.---
Extruder Temp: 205C
Bed Temp: 65C
Speed: 70mm/s
Z-Hop: Enabled
Supports: Disabled
Bed Adhesion: Raft

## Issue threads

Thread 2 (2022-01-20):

### ISSUE TITLE
Conductivity probe mounting

### ISSUE THREAD

**Issue by thomafred** [IanTBlack/CTDizzle#2]
Hi there,

Cool project!

How was the conductivity probe mounted? As far as I understand, the probe is wider than the holes in the end cap

**Comment by IanTBlack** [comment]
If you are using an Atlas Scientific conductivity probe you will need to drill one of the 10mm holes on the end cap to a diameter of 12mm. It looks like Atlas Scientific has changed some things within their datasheet since the CTDizzle was last updated, but drilling to 12mm should hold true for both their "legacy" and current conductivity probes (not the industrial version). I would highly recommend sticking with mm. Their new datasheet inaccurately converts 12mm to 0.5in, while their legacy datasheet resolved it to 0.47in.

A low-end 12mm bit will run you about 10 USD. Another alternative would be to drill out with a 7/16" or 15/32" drillbit (11.11, 11.9 mm respectively) and then use a round file to hand fit the probe to the endcap. If you have access to a drill press, that is optimal. For the version in the [user guide](https://github.com/IanTBlack/CTDizzle/blob/main/documentation/CTDizzle.pdf) I used a cordless drill, which seemed to work fine. I think that after you pot the probe with the PVA molds, the epoxy should fill in any excessive slop between the probe and the drilled hole. Be sure to rough up the surface of the probe that will be in contact with the epoxy.

Let me know if I have answered your question.

Cheers,
- Ian

**Comment by thomafred** [comment]
Awesome, thank you for the clarification!

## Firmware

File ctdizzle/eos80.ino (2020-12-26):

/* The following functions are used to compute depth, salinity, and density using PSS-78 and EOS80 algorithms.
 * They require inputs and do not operate as standalone functions.
 * To compute depth, you will need to first sample pressure.
 * To compute salinity, you will need to first sample conductivity, temperature, and pressure.
 * To compute density, you will need to first sample conductivity, temperature, pressure, and have computed salinity.

Examples on how to compute depth, salinity, and density anomaly.
float depth = compute_depth(p,45.00);
float salinity = compute_salinity(ec,t,p);
float density_anomaly = compute_density_anomaly(salinity,t,p);

*/

float compute_depth(float relative_pressure,float latitude){
  /* Compute the depth in meters using pressure and known latitude. 
   *  Requires a user selected latitude, unless a GPS is integrated and sampled during the setup sequence.
   *  relative_pressure -- a pressure value in decibars. This value is returned when using the get_relative_pressure() function.
   *  latitude -- the known latitude in decimal degrees.
   *  return -- the depth in meters.
   */
  float p = relative_pressure;
  float x = sin(latitude / 57.29578);
  x = x * x;
  float gr = 9.780318 * (1.0 + (5.2788e-3 + 2.36e-5 * x) * x) + 1.092e-6 * p;
  float depth = ((((-1.82e-15 * p + 2.279e-10) * p - 2.2512e-5) * p + 9.72659) * p)/gr;
  return depth;
}

float compute_salinity(float conductivity, float temperature, float relative_pressure){
  /* Compute the salinity using conductivity, temperature and pressure per the PSS-78 formula.
   * ec -- conductivity in uS or uMhos per cm.  This value is returned when using the get_conductivity() function.
   * t -- temperature in degrees Celsius. This value is returned when using the get_temperature() function.
   * p -- pressure in decibars. This value is returned when using the get_relative_pressure() function.
   * return -- the salinity in Practical Salinity Units (PSU).
   */
   float ec = conductivity;
   float t = temperature;
   float p = relative_pressure;
   float A1=2.070e-5, A2=-6.370e-10, A3=3.989e-15;
   float sB1=3.426e-2, sB2=4.464e-1, sB3=4.215e-1, sB4=-3.107e-3;  //Compiler interference requires "B" coeffiecients to be more unique.
   float c0=6.766097e-1, c1=2.00564e-2, c2=1.104259e-4, c3=-6.9698e-7, c4=1.0031e-9;
   float a0=0.0080, a1=-0.1692, a2=25.3851, a3=14.0941, a4=-7.0261, a5=2.7081;
   float b0=0.0005, b1=-0.0056, b2=-0.0066, b3=-0.0375, b4=0.0636, b5=-0.0144;
   float k=0.0162, cstandard=42.914;
  
   float R = ((ec/1000)/cstandard);   
   float rpnum = (A1*p)*(A2*pow(p,2))+(A3*pow(p,3));
   float rpdenom = 1*(sB1*t)+(sB2*pow(t,2))+(sB3*R)+(sB4*t*R);
   float Rp = 1+(rpnum/rpdenom);
   float rT = c0 +(c1*t)+(c2*pow(t,2))+(c3*pow(t,3))+(c4*pow(t,4));
   float RT = R/(rT*Rp);
   float salinity = (a0+(a1*pow(RT,0.5))+(a2*RT)+(a3*pow(RT,1.5))+(a4*pow(RT,2))+(a5*pow(RT,2.5)))+((t-15)/(1+k*(t-15)))*(b0+(b1*pow(RT,0.5))+(b2*RT)+(b3*pow(RT,1.5))+(b4*pow(RT,2))+(b5*pow(RT,2.5)));
   return salinity;
}

float compute_density_anomaly(float salinity, float temperature, float relative_pressure){
  /* Compute density using salinity, temperature, and pressure.
   * salinity -- the known salinity in PSU. This value is returned using the compute_salinity() function.
   * temperature -- the known temperature in degrees Celsius. This value is returned when using the get_temperature() function.
   * relative_pressure -- the known pressure in decibars. This value is returned when using the get_relative_pressure() function.
   * return -- density anomaly.
   */
   float s = salinity;
   float t = temperature;
   float p = relative_pressure;
   float dB0=8.24493e-1, dB1=-4.0899e-3, dB2=7.6438e-5, dB3=-8.2467e-7, dB4=5.3875e-9; //Compiler interference requires "B" coeffiecients to be more unique.
   float C0=-5.72466e-3, C1=1.0227e-4, C2=-1.6546e-6;
   float D0=4.8314e-4;
   float A0=999.842594, A1=6.793952e-2, A2=-9.095290e-3, A3=1.001685e-4, A4=-1.120083e-6, A5=6.536332e-9;
   float FQ0=54.6746, FQ1=-0.603459, FQ2=1.09987e-2, FQ3=-6.1670e-5;
   float G0=7.944e-2, G1=1.6483e-2, G2=-5.3009e-4;
   float i0=2.2838e-3, i1=-1.0981e-5, i2=-1.6078e-6;
   float J0=1.91075e-4;
   float M0=-9.9348e-7, M1=2.0816e-8, M2=9.1697e-10;
   float E0=19652.21, E1=148.4206, E2=-2.327105, E3=1.360477e-2, E4=-5.155288e-5;
   float H0=3.239908, H1=1.43713e-3, H2=1.16092e-4, H3=-5.77905e-7;
   float K0=8.50935e-5, K1=-6.12293e-6, K2=5.2787e-8;

   float t2 = t*t;
   float t3 = t*t2;
   float t4 = t*t3;
   float t5 = t*t4;
   if (s <= 0.0){s = 0.000001;}
   float s32 = pow(s,1.5);
   p = p/10; //Put pressure in bars.
   float sigma = A0 + A1*t + A2*t2 + A3*t3 + A4*t4 + A5*t5 + (dB0 + dB1*t + dB2*t2 + dB3*t3 + dB4*t4)*s + (C0 + C1*t + C2*t2)*s32 + D0*s*s;
   float kw = E0 + E1*t + E2*t2 + E3*t3 + E4*t4;
   float aw = H0 + H1*t + H2*t2 + H3*t3;
   float bw = K0 + K1*t + K2*t2;
   float k = kw + (FQ0 + FQ1*t + FQ2*t2 + FQ3*t3)*s + (G0 + G1*t + G2*t2)*s32 + (aw + (i0 + i1*t + i2*t2)*s + (J0*s32))*p + (bw + (M0 + M1*t + M2*t2)*s)*p*p;
   float val = 1 - p / k;
   if (val){sigma = sigma/val - 1000.0;}   
   return sigma;
}
